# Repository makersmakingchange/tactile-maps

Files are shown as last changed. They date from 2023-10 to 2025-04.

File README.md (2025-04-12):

<!--- Open Source Assistive Technology: GitHub Readme Template --->
<!-- Template files available at https://github.com/makersmakingchange/OpenAT-Template -->

<!--- TITLE Should match the name of the GitHub repository. Choose something descriptive rather than whimsical.  --->
 # Tactile Maps

<!--- SUMMARY A brief summary of the project. What it does, who it is for, how much it costs.  --->
The Tactile Maps are designed to help users with visual impairments learn to navigate different types of intersections with various traffic signs and signals. Maps can be used separately as a learning tool for specific intersections and traffic signs and signals, or can be connected together to plan routes between locations.
The legend includes Braille labels for the different representations of traffic signs and signals.

<!--- PHOTO  --->
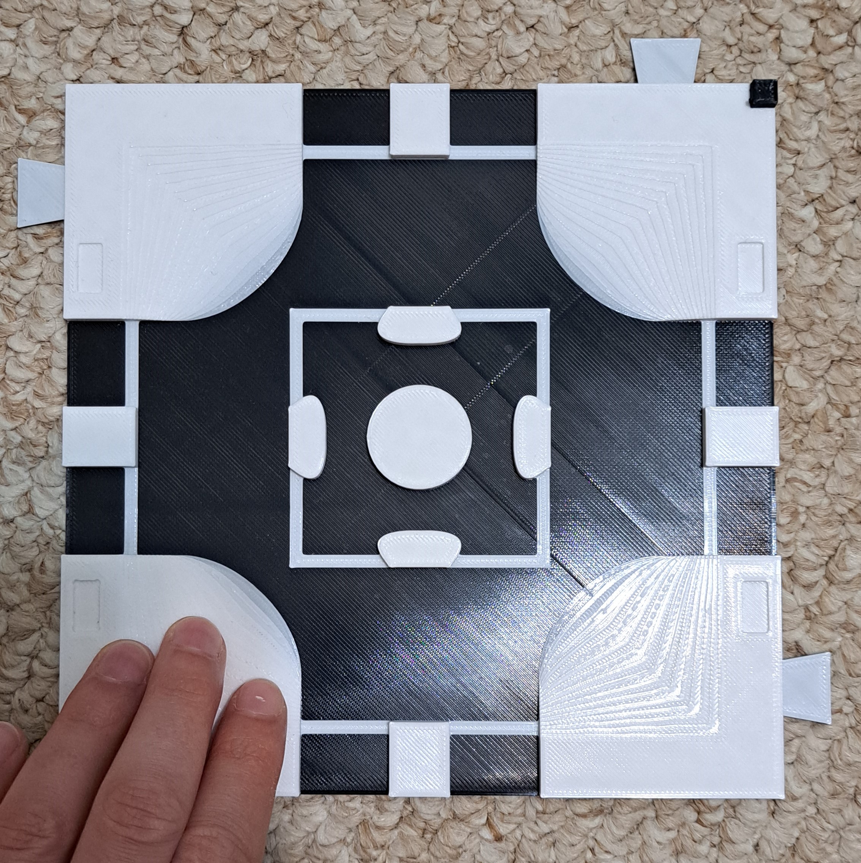
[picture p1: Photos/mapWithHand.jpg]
A user running their hand across the bottom of a tactile map representing a roundabout. The map has been attached to a carpet using hook and loop tape.


## Makers Making Change Assistive Device Library
 - https://www.makersmakingchange.com/s/product/tactile-maps/01tJR000000nEbJYAU

## Getting Started
<!--- 
Include an overall idea of what major steps are required to build the device.
 --->

### 1. Order the Off-The-Shelf Components
The [Bill of Materials](/Documentation/Tactile_Maps_BOM_v1.0.xlsx) lists all of the parts and components required to build the Tactile Maps.

### 2. Print the 3D Printable components
Print the components requested by the user.

All of the files and individual print files can be in the [/Build_Files/3D_Printing_Files](/Build_Files/3D_Printing_Files/) folder.

### 3. Assemble the Tactile Maps.
Reference the [Assembly Guide](/Documentation/Tactile_Maps_Maker_Guide_v1.0.pdf) for the tools and steps required to build the maps.

## Files
<!---
FILES
This section includes all the information and files required to build and modify the device, including documentation, design files, and build files. 
--->

### Documentation
<!---
DOCUMENTATION

--->
| Document | Version | Link |
|----------|---------|------|
| Design Rationale     | 1.0 | [Tactile_Maps_Design_Rationale](/Documentation/Tactile_Maps_Design_Rationale_v0.1.pdf) |
| Bill of Materials    | 1.0 | [Tactile_Maps_BOM](/Documentation/Tactile_Maps_BOM_v0.1.xlsx) |
| Maker Guide       | 1.0 | [Tactile_Maps_Instructions](/Documentation/Tactile_Maps_Maker_Guide_v0.1.pdf) |
| User Guide          | 1.0 | [Tactile_Maps_User_Guide](/Documentation/Tactile_Maps_User_Guide_v1.0.pdf)           |
| Changelog            | 1.0 | [Tactile_Maps_Changelog](/Documentation/Tactile_Maps_Changelog_v0.1.pdf)               |

### Design Files
<!---
DESIGN FILES
If possible, include a copy of original design files to facilitate easy editing and customization.
--->
 - [CAD Files](/Design_Files/CAD)

### Build Files
<!---
BUILD FILES
--->
 - [3D Printing Files](/Build_Files/3D_Printing)

## License
<!---
LICENSE
Choose an appropriate license. We recommend an open-source hardware compatible license.
--->
Everything needed or used to design, make, test, or prepare the Tactile Maps is licensed under the CERN 2.0 2.0 Permissive license <https://ohwr.org/project/cernohl/wikis/Documents/CERN-OHL-version-2> (CERN-OHL-P).

Accompanying material such as instruction manuals, videos, and other copyrightable works that are useful but not necessary to design, make, test, or prepare the Tactile Maps are published under a Creative Commons Attribution-ShareAlike 4.0 license <https://creativecommons.org/licenses/by-sa/4.0/> (CC BY-SA 4.0).

## Attribution
<!-- ATTRIBUTION -->

The documentation template was created by Makers Making Change and is used under a CC BY-SA 4.0 license. It is available at the following link: https://github.com/makersmakingchange/OpenAT-Template

----

<!-- ABOUT MMC START -->
## About Makers Making Change
[Makers Making Change Logo](https://www.makersmakingchange.com/)

Makers Making Change is a program of [Neil Squire](https://www.neilsquire.ca/), a Canadian non-profit that uses technology, knowledge, and passion to empower people with disabilities.

Makers Making Change leverages the capacity of community based Makers, Disability Professionals and Volunteers to develop and deliver affordable Open Source Assistive Technologies.

 - Website: [www.MakersMakingChange.com](https://www.makersmakingchange.com/)
 - GitHub: [makersmakingchange](https://github.com/makersmakingchange)
 - Bluesky: [@makersmakingchange.bsky.social](https://bsky.app/profile/makersmakingchange.bsky.social)
 - Instagram: [@makersmakingchange](https://www.instagram.com/makersmakingchange)
 - Facebook: [makersmakechange](https://www.facebook.com/makersmakechange)
 - LinkedIn: [Neil Squire Society](https://www.linkedin.com/company/neil-squire-society/)
 - Thingiverse: [makersmakingchange](https://www.thingiverse.com/makersmakingchange/about)
 - Printables: [MakersMakingChange](https://www.printables.com/@MakersMakingChange)

### Contact Us
For technical questions, to get involved, or to share your experience we encourage you to [visit our website](https://www.makersmakingchange.com/) or [contact us](https://www.makersmakingchange.com/s/contact).
<!-- ABOUT MMC END -->

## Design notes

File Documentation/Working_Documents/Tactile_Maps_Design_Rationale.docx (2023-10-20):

# Introduction

Tactile maps are often used to teach people with visual impairments how to navigate their surroundings. These maps can represent specific indoor and outdoor locations, or represent general information, such as a type of road intersection. Orientation and Mobility (OM) specialists often use tactile maps with their clients, but diagraming tools they use are not given to clients to take home and learn from. We wanted to create general maps of different road intersections that OM specialists could use with clients to teach how to navigate various generic intersections.

The tactile maps are intended for users with visual impairments. The maps could be used independently by people with visual impairments to study different types of intersections and can be used by OM specialists with clients.

It is important to note these maps are not designed to be an independent navigational tool. They are intended to help teach common features of different types of road intersections to help users with visual impairment learn to recognize different intersections. Relying on the maps for navigation could cause potential harm to users, such as getting lost or misidentifying an intersection.

# Research

Title | Touch Mapper
Link | https://touch-mapper.org/en/
Author | Samuli Pahaoja
License | Not stated, but open source
Cost | Cost of material, or starting at $29 USD for a printed map
Test Build (Y/N) | Y
Add to Library (Y/N) | N
Notes | Only outdoor maps are supported currently. Scale of maps are customizable, and maps can be printed in multiple parts. Maps do not include Braille labels or space for labels.

Title | Tactile Map Automated Production (TMAP)
Link | https://lighthouse-sf.org/tmap/
Author | Lighthouse for the Blind and Visually Impaired
License | Not listed
Cost | $26.25 USD for printed map, cost of materials if building own.
Test Build (Y/N) | N
Add to Library (Y/N) | N
Notes | Maps include Braille labels and legend. Maps designed to be embossed or printed on swell paper, not 3D printed.

Title | Picture Maker Wheatley Tactile Diagramming Kit
Link | https://www.aph.org/product/picture-maker-wheatley-tactile-diagramming-kit/
Author | Picture Maker
License | Not stated
Cost | $183 USD
Notes | Can quickly create tactile maps using pieces that attach to a felt background. Comes with various pieces that are simple shapes and high contrast colours.

# Requirements

## Goals

G01 | Create tactile maps of generic intersections (roundabouts, 4-way-stops, T-intersections, offset intersections, pedestrian crossings, and large intersections with corner islands)
G02 | Create representations of traffic signs/signals and common landmarks (bus stops, mailboxes)
G03 | Help users learn to navigate different intersections

## Functional Requirements

F01 | Features must be large enough and have enough space around them to be easily identified and differentiated through touch
F02 | Maps must be durable
F03 | Maps must accurately represent their respective intersections
F04 | Maps must include a legend to identify features such as traffic signs/signals
F05 | Maps should be simple to print in high contrast colours for users with partial sight

## Non-functional Requirement

NF01 | Maps must be easy to clean
NF02 | Maps must be easy to transport

## Constraints

C01 | Maps cannot contain too much information as they can become cluttered and difficult to interpret by touch
C02 | Maps must be low-cost

# Ideation

First concepts involved working from maps built through Touch Mapper, or through adapting Touch Mapper to suit the needs of the users. This idea was abandoned as it required a strong background in Python coding to adapt Touch Mapper, and converting STLs to modifiable models was computationally expensive. Creating the maps entirely was deemed to be both faster and a more suitable option for meeting the requestor’s needs.

# Conceptual Design

## Concept 1: Individual Maps

Initially, maps were designed to be individual pieces representing a specific intersection. These maps were designed to teach users common features of each intersection type.

## Concept 2: Connectable Maps

The second concept was to make maps which could be connected to build out routes between places. These would allow users to plan how they could move from one place to another by identifying the number and types of intersections they would need to pass through.

It is important to note that the maps should be considered a rough guide only and should not be used alone for route planning and navigation. Misidentifying the type and number of intersections on a route could cause a user to get lost or potentially come in harms way from crossing an intersection incorrectly.

# Prototyping

The first two prototypes were created to test the size of maps, height of the features, colour contrast, and the inclusion of Braille labels on the map. The larger map was 17x17x0.6 cm, and the smaller map was 8.5x8.5x0.32 cm. The maps also included Braille labels identifying the type of intersection they represented. There were not tabs used to connect the maps together as they were different sizes. The two prototypes are shown below:

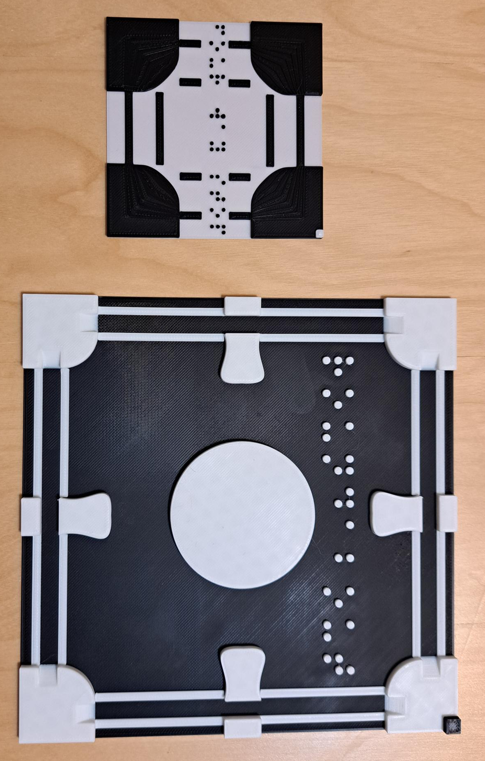
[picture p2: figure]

# Testing

The two prototype maps were sent to Orientation and Mobility specialists at Vision Loss Rehab in Burnaby, British Columbia. The users preferred the size of the larger map and the height of the features on that map. They also did not like having the Braille label in the middle of the map, as they felt users could have trouble differentiating the Braille labels from a feature on the map. The users also preferred the maps printed with white on black to the maps printed black on white. The subsequent maps were created at the size of the larger map, and Braille labels were removed from the maps themselves.

The clearance required for the pieces that insert into the maps, and the Braille labels for the legends were also tested. A clearance of 0.2 mm on each dimension, and dog boning of the holes with a 2 mm cutting tool diameter were found to be sufficient for a tight fit that was still easily removable.

# Detailed Design

All the maps use the same parameters, which can be found in the Fusion 360 file: TactileMapsParameters. The parameters are pulled from this file into all the others, so if someone wants to update the same parameter in all maps, they can update the TactileMapsParameters file only. The parameters are listed in the table below for users who do not have Fusion 360. Many of the parameters are built off others, such as the sidewalkWidth being one third of the length of the model.

Parameter Name | Value (mm) | Description
baseHeight | 0.4 | Height of the base of the model
clearance | 0.2 | Clearance around parts that will fit together
dogbone | 2 | Cutter diameter for creating dogbone corners.
featureHeight | 1.6 | Height of features such as bus stops
length | 170 | Side lengths of base of model
lineHeight | 0.3 | Height of crosswalk lines
lineWidth | 3 | Width of crosswalk lines
orientorHeight | 2.4 | Height of the orientation indicator
orientorSize | 6 | Side length of orientation indicator square
pegDepth | sidewalkHeight/4 | Depth of pegs/holes to connect features to map base
pegSize | 6 | Side length of pegs/holes to connect features to map base
sidewalkHeight | 3.2 | Height of sidewalk/walking surface
sidewalkWidth | length/3 | Width of the sidewalk/walking surface
tabHeight | sidewalkHeight/4 | Height of tabs to secure adjacent maps together
tabLength | length/14 | Length of tab to secure adjacent maps together
tabWidth | length/10 | Width of tabs to secure adjacent maps together

All the tactile maps have the road surface as the lowest surface, with any features raised above that. Painted pedestrian crossing lines are the second lowest feature and are raised to be felt by the user. Sidewalks and curbs are the third lowest feature, with curb cuts represented as gradual height increases and curbs as sudden changes in height (as they are in the real world). The features that can be slotted into the cut-outs on the sidewalks are the second highest level, allowing users to feel where and what a traffic sign may be. The highest feature on the map is a square in the top-right corner. This is used to orient the map and can represent North-East if planning a route. There are also tabs and cut-outs on the maps to connect and align them if they are being used together for route planning. All features are shown in the figures below.

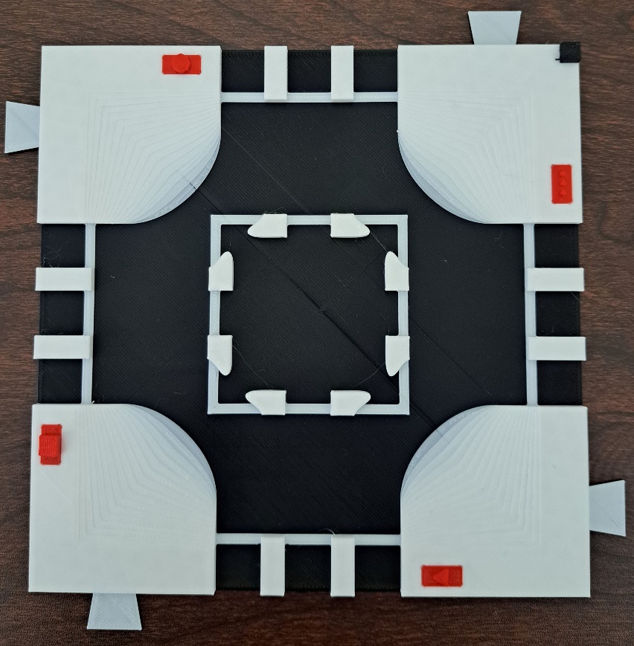
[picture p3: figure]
A tactile map of a large intersection. Different features are highlighted with different shaped boxes. A tab on the side used to connect maps together is circled in red, a stop sign piece is surrounded by a red rectangle, and the orientation indicator is surrounded by a red triangle.

The tabs on the sides of the maps are used to connect maps together. One of the tabs (top left) is circled in red. There are red pieces representing a stop sign, stop light, yield sign, and mailbox added to the map. The stop sign piece is surrounded by a red square. These pieces can be interchanged among maps and positions on the maps. The orientation square in the top right is surrounded by a red triangle.

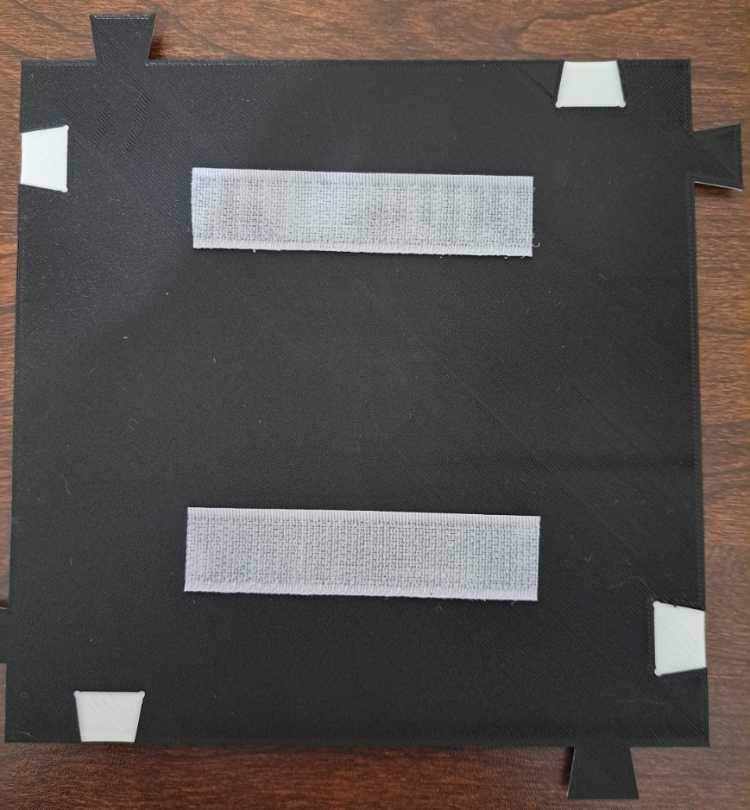
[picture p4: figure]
Hook side of hook and loop tape attached to the back of a tactile map. The cut-outs where tabs connect adjacent maps are circled in red.

The bottom of the map shows the corresponding cut-outs for the tabs on the sides. The tabs fit into the cut-outs to prevent the maps from shifting while users run their fingers over them. The cut-out on the top left has been circled in red. There is also hook and loop tape attached to the bottom of the map to allow it to be mounted to another surface. The hook side of the tape has been connected to the map.

There is also a legend with Braille labels to help users identify different features such as traffic signs/signals.

From top to bottom the symbols represent a stop sign, a yield sign, a mailbox, a bus stop, a bike lane, a stop light, rail tracks, and a pedestrian crossing. The labels read: “stop”, “yield”, “mailbox”, “bus stop”, “bike lane”, “stop light”, “rail crossing”, and “pedestrian crossing”.

# Opportunities for Improvement

- Improving alignment/connection design
  - Current tabs can break easily
  - Current tabs could connect maps more securely
  - Could use bowtie shaped pieces to hold the maps together
- Including method to create custom maps for individual users (with Orientation and Mobility specialist consultation)
- Including space for 3D printed Braille labels for each map
- Create standard text tactile legend

© 2023 by Neil Squire. This work is licensed under the CC BY SA 4.0 License: http://creativecommons.org/licenses/by-sa/4.0 Files available at https://makersmakingchange.com/project/tactile-maps/ Page 1 of 1

V1.0 | May 2023 Tactile Maps Design Rationale

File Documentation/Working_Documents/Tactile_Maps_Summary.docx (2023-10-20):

# Title

Tactile Maps

## Subtitle

3D printed Tactile Maps for people with visual impairments. The general maps represent different intersections and common road signs.

## Device Specifications

Build Time:

< 1hr

1-4 hr

5-10hr

>10hr

Cost:

$0 - $10

$11 - $25

$26 - $50

$51 - $100

$101 - $250

$250+

Stage:

- Recently added

Skills:

- 3D printing

Need:

- Orientation and mobility

Disability:

- Visual impairment

Difficulty:

- Easy

License:

- Attribution – ShareAlike 4.0 International

Usages:

- Orientation and mobility

Type:

- Assistive device

Designer:

- Stephan Dobri – Makers Making Change

## Device Details

### Overview

The Tactile Maps are designed to help users with visual impairments learn to navigate different types of intersections with various traffic signs and signals. Maps can be used separately as a learning tool for specific intersections and traffic signs and signals, or can be connected together to plan routes between locations.

The legend includes Braille labels for the different representations of traffic signs and signals.

### Usage

Use the map on a surface where it will not slide around as the user runs their hands over the map. If the map has hook and loop tape, the maps can be attached to any surface the hook side will attach to, including carpet or tactile map diagramming kit backboards. Insert the desired traffic sign/signal pieces into the spaces on the tactile maps being used. The pieces should fit snuggly into the cut-outs on the tops of the maps and not get knocked out when running your hand over the features. They should still be easy to remove and change different pieces.

There is a raised square in the top-right corner of the map to help users orient to the direction of the maps. For example, this corner could represent North-East.

A user will run their hands over the maps to feel the different road features, including crosswalk lines, sidewalks/pavement, and traffic signs/signals.

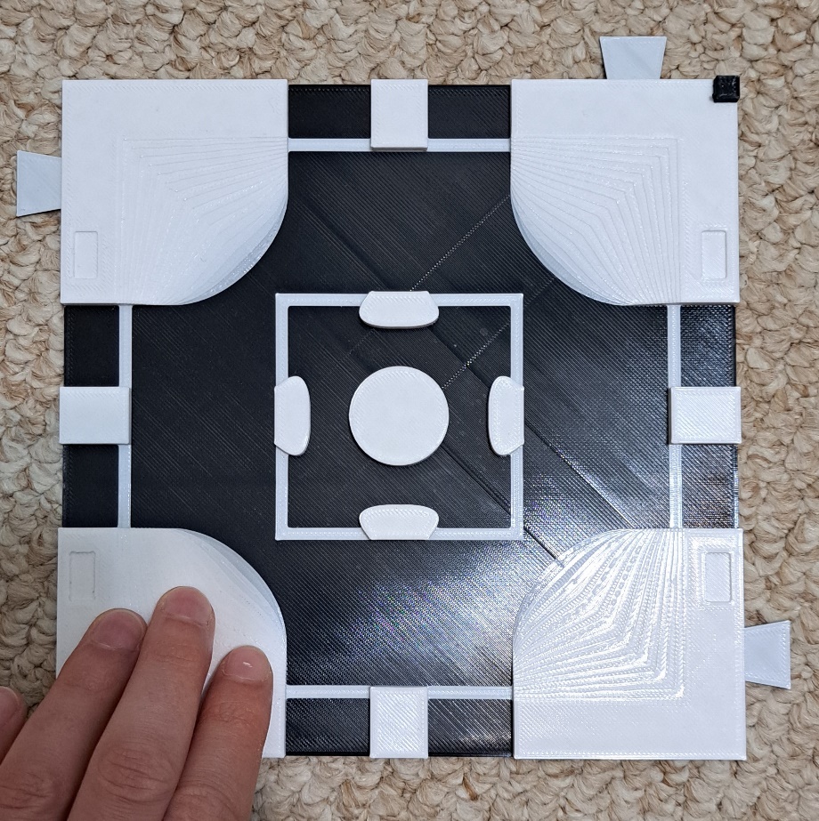
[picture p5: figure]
A user running their hand across the bottom of a tactile map representing a roundabout. The map has been attached to a carpet using hook and loop tape.

If they are unsure what a feature represents, they can consult the legend if they read Braille. If they do not read Braille, the different signs and signals are shown below.

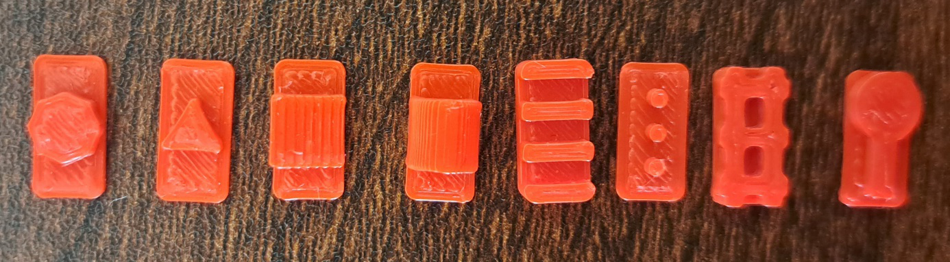
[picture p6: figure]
3D printed features that represent from left to right: Stop signs, yield signs, mailboxes, bus stops, bike lanes, stop signs, railroad crossings, and pedestrian crossings.

3D printed features that represent from left to right: Stop signs, yield signs, mailboxes, bus stops, bike lanes, stop signs, railroad tracks, and pedestrian crossings.

Maps can also be connected to represent a route between places in a city. For example, if someone had to walk through an offset intersection then to a pedestrian crossing, the two maps could be connected as shown below.

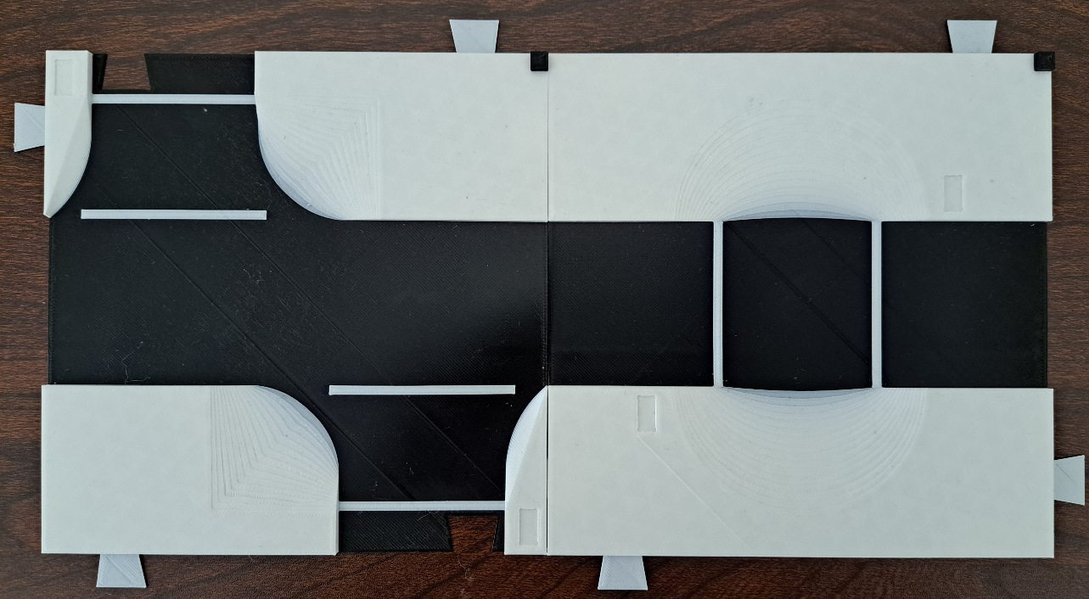
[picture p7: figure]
Two tactile maps connected together by the tabs on the edges of the maps. The two maps represent an offset intersection and pedestrian crossing.

### Cost

Printing all six tactile maps, the legend, Braille labels, and feature pieces, and adding hook and loop tape to each map and the legend costs $13.00. If a user does not want hook and loop tape, or a different combination of maps and features the cost will change.

### Build Instructions

This build consists solely of 3D printing.

#### Skills Required

3D printing

#### Time Required

The total time to print all six maps, the legend, Braille labels, and feature pieces is 35 hours and 20 minutes. There is a detailed breakdown of how long each piece takes to print in the Bill of Materials (BOM), and Maker Guide.

Assembling the legend will take under five minutes.

#### Tools

Scissors (optional)

Super glue (optional)

#### Components

Hook and loop tape (optional)

#### 3D Printing

- Tactile maps legend
- Four way stop map
- Large intersection map
- Offset intersection map
- Pedestrian crossing map
- Roundabout map
- T-intersection map
- Bike lane piece
- Bike lane label
- Bus stop piece
- Bus stop label
- Mailbox piece
- Mailbox label
- Pedestrian crossing piece
- Pedestrian crossing label
- Rail crossing piece
- Rail crossing label
- Stop light piece
- Stop light label
- Stop sign piece
- Stop sign label
- Yield sign piece
- Yield sign label

### Design

### Attribution

This design was requested by employees of Vision Loss Rehab in British Columbia.

Original design by: Stephan Dobri – Makers Making Change under an Attribution – ShareAlike 4.0 International license.

The orientation indicator was based on the indicator used by Touch Mapper (https://touch-mapper.org/en/).

© 2023 by Neil Squire. This work is licensed under the CC BY SA 4.0 License: http://creativecommons.org/licenses/by-sa/4.0 Files available at https://makersmakingchange.com/project/tactile-maps/ Page 1 of 2

V1.0 | May 2023 Tactile Maps Summary

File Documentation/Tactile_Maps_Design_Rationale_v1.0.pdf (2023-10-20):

V1.0 | May 2023

## Tactile Maps

## DESIGN RATIONALE

© 2023 by Neil Squire. (https://neilsquire.ca/)
This work is licensed under the CC BY SA 4.0 License: http://creativecommons.org/licenses/by-sa/4.0 Files available at https://makersmakingchange.com/project/tactile-maps/

### Introduction

Tactile maps are often used to teach people with visual impairments how to navigate their surroundings. These maps can represent specific indoor and outdoor locations, or represent general information, such as a type of road intersection. Orientation and Mobility (OM) specialists often use tactile maps with their clients, but diagraming tools they use are not given to clients to take home and learn from. We wanted to create general maps of different road intersections that OM specialists could use with clients to teach how to navigate various generic intersections.

The tactile maps are intended for users with visual impairments. The maps could be used independently by people with visual impairments to study different types of intersections and can be used by OM specialists with clients.

It is important to note these maps are not designed to be an independent navigational tool. They are intended to help teach common features of different types of road intersections to help users with visual impairment learn to recognize different intersections. Relying on the maps for navigation could cause potential harm to users, such as getting lost or misidentifying an intersection.

### Research

Title | Touch Mapper
Link | https://touch-mapper.org/en/
Author | Samuli Pahaoja
License | Not stated, but open source
Cost | Cost of material, or starting at $29 USD for a printed map
Test Build (Y/N) | Y
Add to Library (Y/N) | N
Notes | Only outdoor maps are supported currently. Scale of maps are customizable, and maps can be printed in multiple parts. Maps do not include Braille labels or space for labels.
Title | Tactile Map Automated Production (TMAP)
Link | https://lighthouse-sf.org/tmap/
Author | Lighthouse for the Blind and Visually Impaired
License | Not listed
Cost | $26.25 USD for printed map, cost of materials if building own.
Test Build (Y/N) | N
Add to Library (Y/N) | N

## DESIGN RATIONALE

© 2023 by Neil Squire. (https://neilsquire.ca/)

Notes | Maps include Braille labels and legend. Maps designed to be embossed or printed on swell paper, not 3D printed.
Title | Picture Maker Wheatley Tactile Diagramming Kit
Link | https://www.aph.org/product/picture-maker-wheatley-tactile-diagramming-kit/ (https://www.aph.org/product/picture-maker-wheatley-tactile-diagramming-kit/)
Author | Picture Maker
License | Not stated
Cost | $183 USD
Notes | Can quickly create tactile maps using pieces that attach to a felt background. Comes with various pieces that are simple shapes and high contrast colours.

### Requirements

### Goals

G01 | Create tactile maps of generic intersections (roundabouts, 4-way-stops, T-intersections, offset intersections, pedestrian crossings, and large intersections with corner islands)
G02 | Create representations of traffic signs/signals and common landmarks (bus stops, mailboxes)
G03 | Help users learn to navigate different intersections

### Functional Requirements

F01 | Features must be large enough and have enough space around them to be easily identified and differentiated through touch
F02 | Maps must be durable
F03 | Maps must accurately represent their respective intersections
F04 | Maps must include a legend to identify features such as traffic signs/signals
F05 | Maps should be simple to print in high contrast colours for users with partial sight

### Non-functional Requirement

NF01 | Maps must be easy to clean
NF02 | Maps must be easy to transport

### Constraints

C01 Maps cannot contain too much information as they can become cluttered and difficult to interpret by touch

## DESIGN RATIONALE

© 2023 by Neil Squire. (https://neilsquire.ca/)

C02 Maps must be low-cost

### Ideation

First concepts involved working from maps built through Touch Mapper, or through adapting Touch Mapper to suit the needs of the users. This idea was abandoned as it required a strong background in Python coding to adapt Touch Mapper, and converting STLs to modifiable models was computationally expensive. Creating the maps entirely was deemed to be both faster and a more suitable option for meeting the requestor’s needs.

### Conceptual Design

### Concept 1: Individual Maps

Initially, maps were designed to be individual pieces representing a specific intersection. These maps were designed to teach users common features of each intersection type.

### Concept 2: Connectable Maps

The second concept was to make maps which could be connected to build out routes between places. These would allow users to plan how they could move from one place to another by identifying the number and types of intersections they would need to pass through.

It is important to note that the maps should be considered a rough guide only and should not be used alone for route planning and navigation. Misidentifying the type and number of intersections on a route could cause a user to get lost or potentially come in harms way from crossing an intersection incorrectly.

### Prototyping

The first two prototypes were created to test the size of maps, height of the features, colour contrast, and the inclusion of Braille labels on the map. The larger map was 17x17x0.6 cm, and the smaller map was 8.5x8.5x0.32 cm. The maps also included Braille labels identifying the type of intersection they represented. There were not tabs used to connect the maps together as they were different sizes. The two prototypes are shown below:

## DESIGN RATIONALE

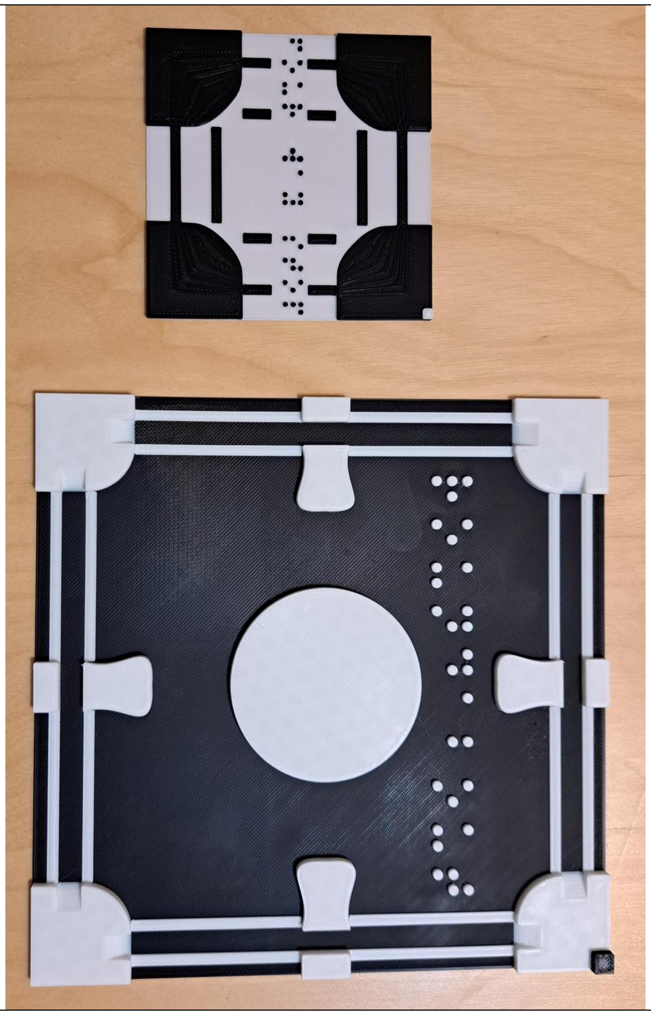
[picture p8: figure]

© 2023 by Neil Squire. (https://neilsquire.ca/)

### Testing

The two prototype maps were sent to Orientation and Mobility specialists at Vision Loss Rehab in Burnaby, British Columbia. The users preferred the size of the larger map and the height of the features on that map. They also did not like having the Braille label in the middle of the map, as they felt users

## DESIGN RATIONALE

© 2023 by Neil Squire. (https://neilsquire.ca/)

could have trouble differentiating the Braille labels from a feature on the map. The users also preferred the maps printed with white on black to the maps printed black on white. The subsequent maps were created at the size of the larger map, and Braille labels were removed from the maps themselves.

The clearance required for the pieces that insert into the maps, and the Braille labels for the legends were also tested. A clearance of 0.2 mm on each dimension, and dog boning of the holes with a 2 mm cutting tool diameter were found to be sufficient for a tight fit that was still easily removable.

### Detailed Design

All the maps use the same parameters, which can be found in the Fusion 360 file: TactileMapsParameters. The parameters are pulled from this file into all the others, so if someone wants to update the same parameter in all maps, they can update the TactileMapsParameters file only. The parameters are listed in the table below for users who do not have Fusion 360. Many of the parameters are built off others, such as the sidewalkWidth being one third of the length of the model.

Parameter Name | Value (mm) | Description
baseHeight | 0.4 | Height of the base of the model
clearance | 0.2 | Clearance around parts that will fit together
dogbone | 2 | Cutter diameter for creating dogbone corners.
featureHeight | 1.6 | Height of features such as bus stops
length | 170 | Side lengths of base of model
lineHeight | 0.3 | Height of crosswalk lines
lineWidth | 3 | Width of crosswalk lines
orientorHeight | 2.4 | Height of the orientation indicator
orientorSize | 6 | Side length of orientation indicator square
pegDepth | sidewalkHeight/4 | Depth of pegs/holes to connect features to map base
pegSize | 6 | Side length of pegs/holes to connect features to map base
sidewalkHeight | 3.2 | Height of sidewalk/walking surface
sidewalkWidth | length/3 | Width of the sidewalk/walking surface
tabHeight | sidewalkHeight/4 | Height of tabs to secure adjacent maps together
tabLength | length/14 | Length of tab to secure adjacent maps together

## DESIGN RATIONALE

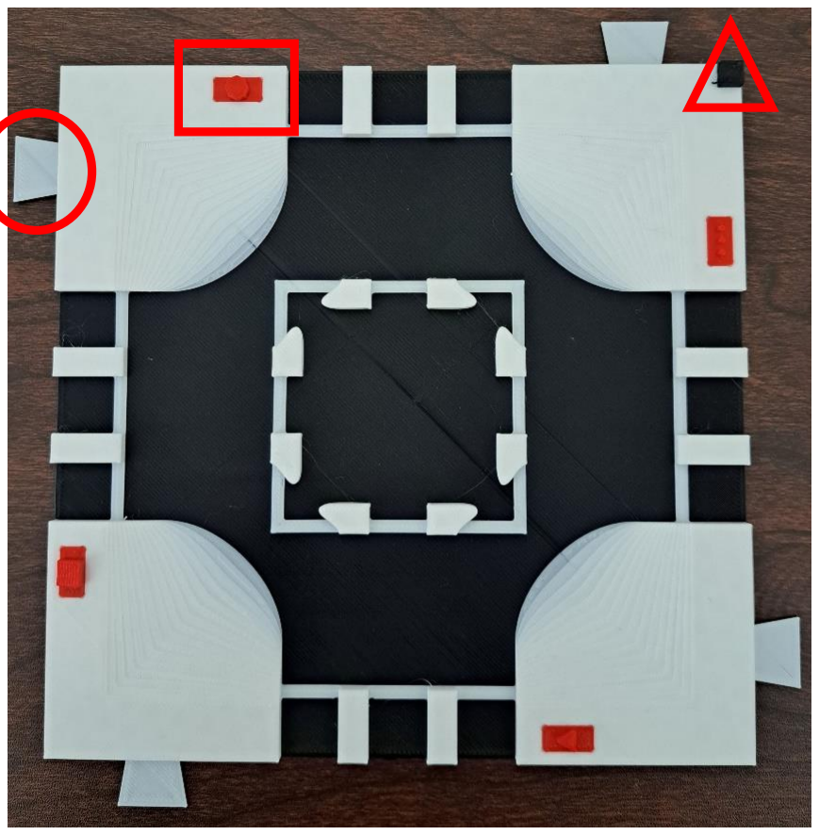
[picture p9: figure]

© 2023 by Neil Squire. (https://neilsquire.ca/)

tabWidth | length/10 | Width of tabs to secure adjacent maps together

All the tactile maps have the road surface as the lowest surface, with any features raised above that. Painted pedestrian crossing lines are the second lowest feature and are raised to be felt by the user. Sidewalks and curbs are the third lowest feature, with curb cuts represented as gradual height increases and curbs as sudden changes in height (as they are in the real world). The features that can be slotted into the cut-outs on the sidewalks are the second highest level, allowing users to feel where and what a traffic sign may be. The highest feature on the map is a square in the top-right corner. This is used to orient the map and can represent North-East if planning a route. There are also tabs and cut-outs on the maps to connect and align them if they are being used together for route planning. All features are shown in the figures below.

The tabs on the sides of the maps are used to connect maps together. One of the tabs (top left) is circled in red. There are red pieces representing a stop sign, stop light, yield sign, and mailbox added to the map. The stop sign piece is surrounded by a red square. These pieces can be interchanged among maps and positions on the maps. The orientation square in the top right is surrounded by a red triangle.

## DESIGN RATIONALE

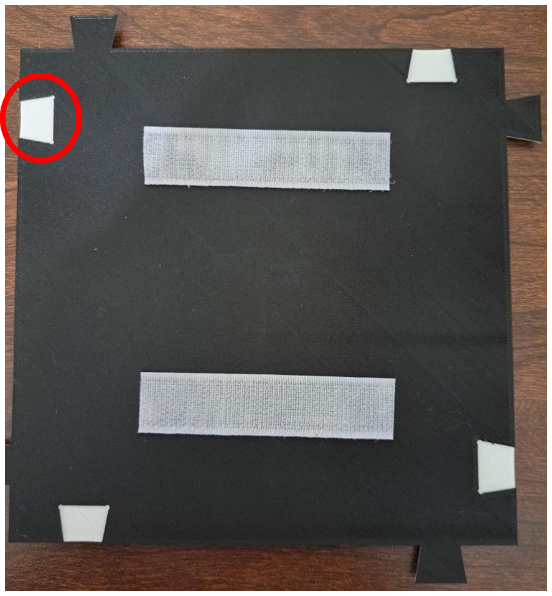
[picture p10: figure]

© 2023 by Neil Squire. (https://neilsquire.ca/)

The bottom of the map shows the corresponding cut-outs for the tabs on the sides. The tabs fit into the cut-outs to prevent the maps from shifting while users run their fingers over them. The cut-out on the top left has been circled in red. There is also hook and loop tape attached to the bottom of the map to allow it to be mounted to another surface. The hook side of the tape has been connected to the map.

There is also a legend with Braille labels to help users identify different features such as traffic signs/signals.

From top to bottom the symbols represent a stop sign, a yield sign, a mailbox, a bus stop, a bike lane, a stop light, rail tracks, and a pedestrian crossing. The labels read: “stop”, “yield”, “mailbox”, “bus stop”, “bike lane”, “stop light”, “rail crossing”, and “pedestrian crossing”.

### Opportunities for Improvement

- Improving alignment/connection design
- Current tabs can break easily
- Current tabs could connect maps more securely

## DESIGN RATIONALE

© 2023 by Neil Squire. (https://neilsquire.ca/)

- Could use bowtie shaped pieces to hold the maps together
- Including method to create custom maps for individual users (with Orientation and Mobility specialist consultation)
- Including space for 3D printed Braille labels for each map
- Create standard text tactile legend

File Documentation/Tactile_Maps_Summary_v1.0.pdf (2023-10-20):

V1.0 | May 2023

## Tactile Maps

## SUMMARY

© 2023 by Neil Squire. (https://neilsquire.ca/)
This work is licensed under the CC BY SA 4.0 License: http://creativecommons.org/licenses/by-sa/4.0 Files available at https://makersmakingchange.com/project/tactile-maps/

### Title

Tactile Maps

### Subtitle

3D printed Tactile Maps for people with visual impairments. The general maps represent different intersections and common road signs.

### Device Specifications

Build Time:

< 1hr

1-4 hr

5-10hr

>10hr

Cost:

$0 - $10

$11 - $25

$26 - $50

$51 - $100

$101 - $250

$250+

Stage:

- Recently added

Skills:

- 3D printing

Need:

- Orientation and mobility

Disability:

- Visual impairment

## SUMMARY

© 2023 by Neil Squire. (https://neilsquire.ca/)

Difficulty:

- Easy

License:

- Attribution – ShareAlike 4.0 International

Usages:

- Orientation and mobility

Type:

- Assistive device

Designer:

- Stephan Dobri – Makers Making Change

### Device Details

Overview
The Tactile Maps are designed to help users with visual impairments learn to navigate different types of intersections with various traffic signs and signals. Maps can be used separately as a learning tool for specific intersections and traffic signs and signals, or can be connected together to plan routes between locations.

The legend includes Braille labels for the different representations of traffic signs and signals.

Usage
Use the map on a surface where it will not slide around as the user runs their hands over the map. If the map has hook and loop tape, the maps can be attached to any surface the hook side will attach to, including carpet or tactile map diagramming kit backboards. Insert the desired traffic sign/signal pieces into the spaces on the tactile maps being used. The pieces should fit snuggly into the cut-outs on the tops of the maps and not get knocked out when running your hand over the features. They should still be easy to remove and change different pieces.

There is a raised square in the top-right corner of the map to help users orient to the direction of the maps. For example, this corner could represent North-East.

A user will run their hands over the maps to feel the different road features, including crosswalk lines, sidewalks/pavement, and traffic signs/signals.

## SUMMARY

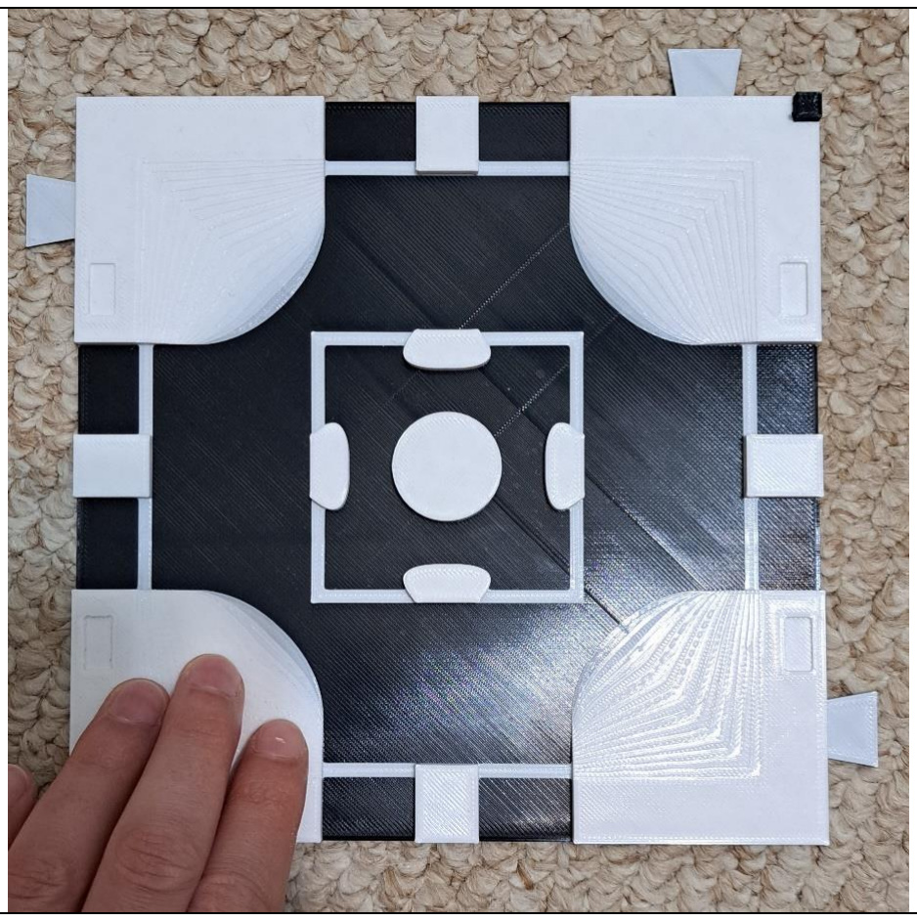
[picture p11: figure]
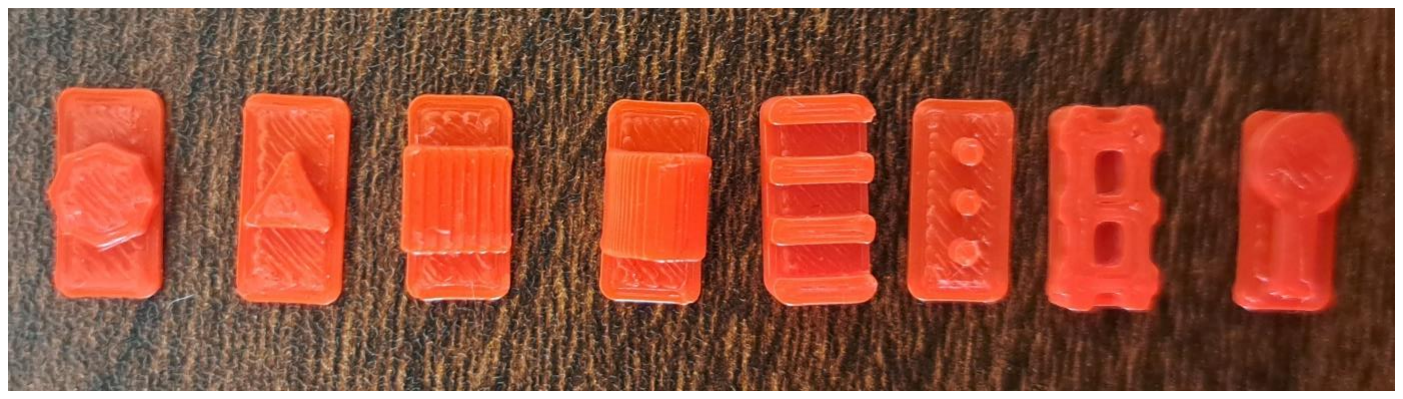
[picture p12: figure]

© 2023 by Neil Squire. (https://neilsquire.ca/)

If they are unsure what a feature represents, they can consult the legend if they read Braille. If they do not read Braille, the different signs and signals are shown below.

3D printed features that represent from left to right: Stop signs, yield signs, mailboxes, bus stops, bike lanes, stop signs, railroad tracks, and pedestrian crossings.

Maps can also be connected to represent a route between places in a city. For example, if someone had to walk through an offset intersection then to a pedestrian crossing, the two maps could be connected as shown below.

## SUMMARY

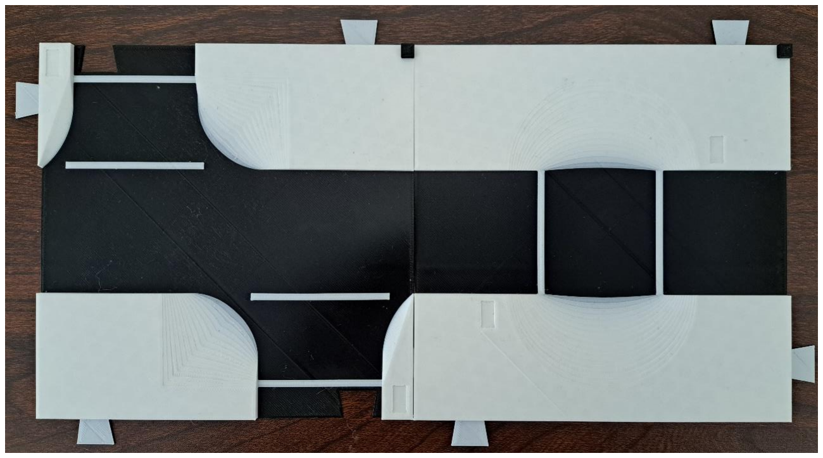
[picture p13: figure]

© 2023 by Neil Squire. (https://neilsquire.ca/)

Cost
Printing all six tactile maps, the legend, Braille labels, and feature pieces, and adding hook and loop tape to each map and the legend costs $13.00. If a user does not want hook and loop tape, or a different combination of maps and features the cost will change.

Build Instructions
This build consists solely of 3D printing.

Skills Required
3D printing

Time Required
The total time to print all six maps, the legend, Braille labels, and feature pieces is 35 hours and 20 minutes. There is a detailed breakdown of how long each piece takes to print in the Bill of Materials (BOM), and Maker Guide.

Assembling the legend will take under five minutes.

Tools
Scissors (optional)

Super glue (optional)

## SUMMARY

© 2023 by Neil Squire. (https://neilsquire.ca/)

Components
Hook and loop tape (optional)

3D Printing
- Tactile maps legend
- Four way stop map
- Large intersection map
- Offset intersection map
- Pedestrian crossing map
- Roundabout map
- T-intersection map
- Bike lane piece
- Bike lane label
- Bus stop piece
- Bus stop label
- Mailbox piece
- Mailbox label
- Pedestrian crossing piece
- Pedestrian crossing label
- Rail crossing piece
- Rail crossing label
- Stop light piece
- Stop light label
- Stop sign piece
- Stop sign label
- Yield sign piece
- Yield sign label

Design

Attribution
This design was requested by employees of Vision Loss Rehab in British Columbia.

Original design by: Stephan Dobri – Makers Making Change under an Attribution – ShareAlike 4.0 International license.

The orientation indicator was based on the indicator used by Touch Mapper. (https://touch-mapper.org/en/)

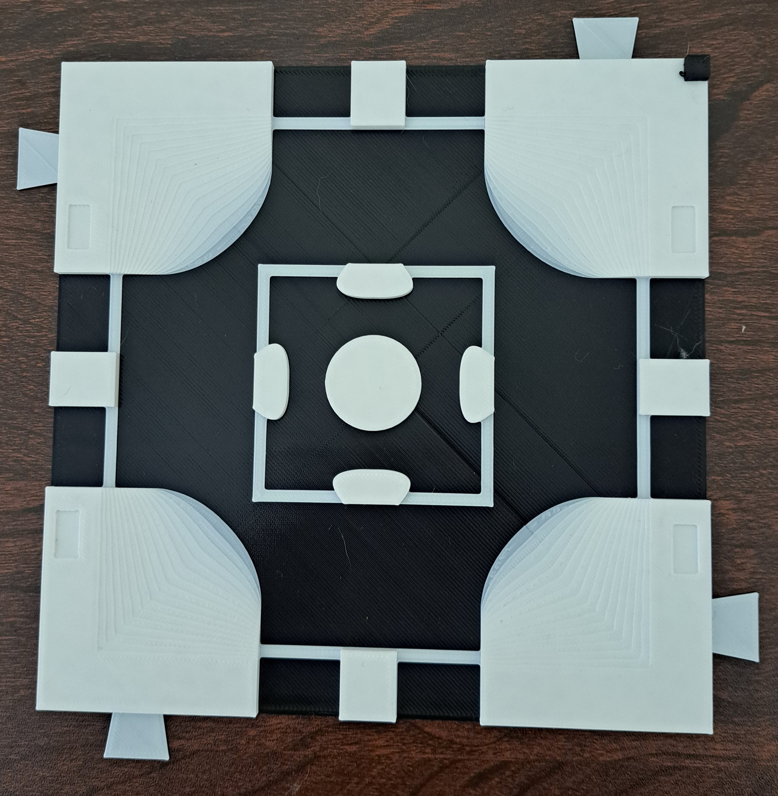
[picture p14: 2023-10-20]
Photos/Roundabout.jpg

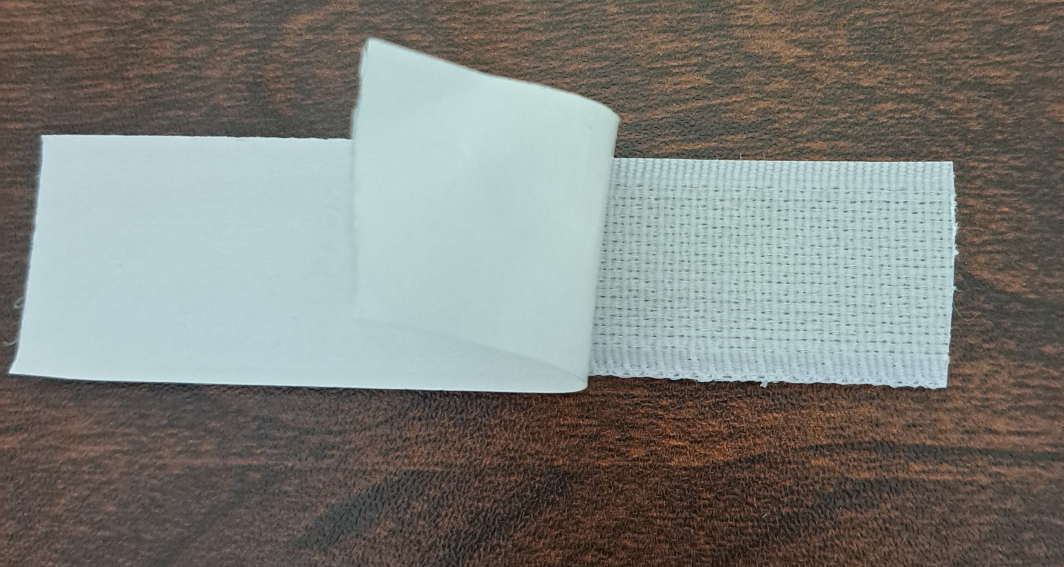
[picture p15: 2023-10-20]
Photos/peelingHook.jpg

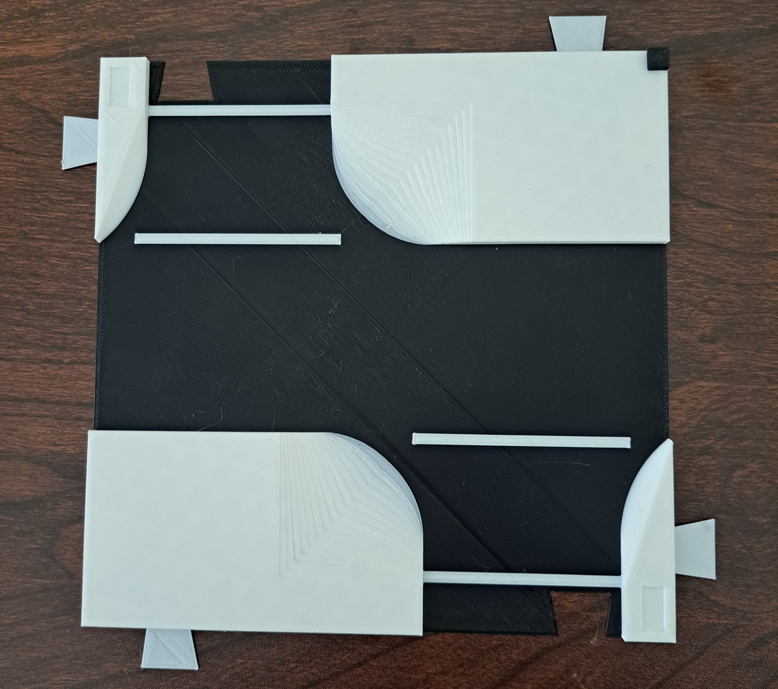
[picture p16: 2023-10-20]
Photos/offsetIntersection.jpg

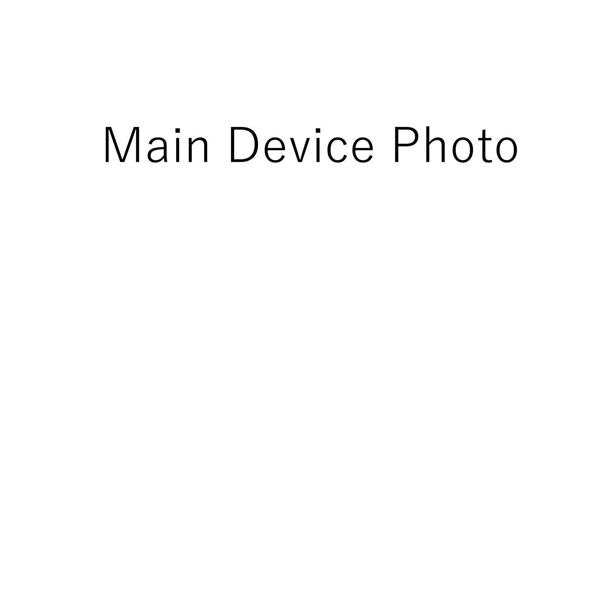
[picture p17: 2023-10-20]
Photos/Device-Name.jpg

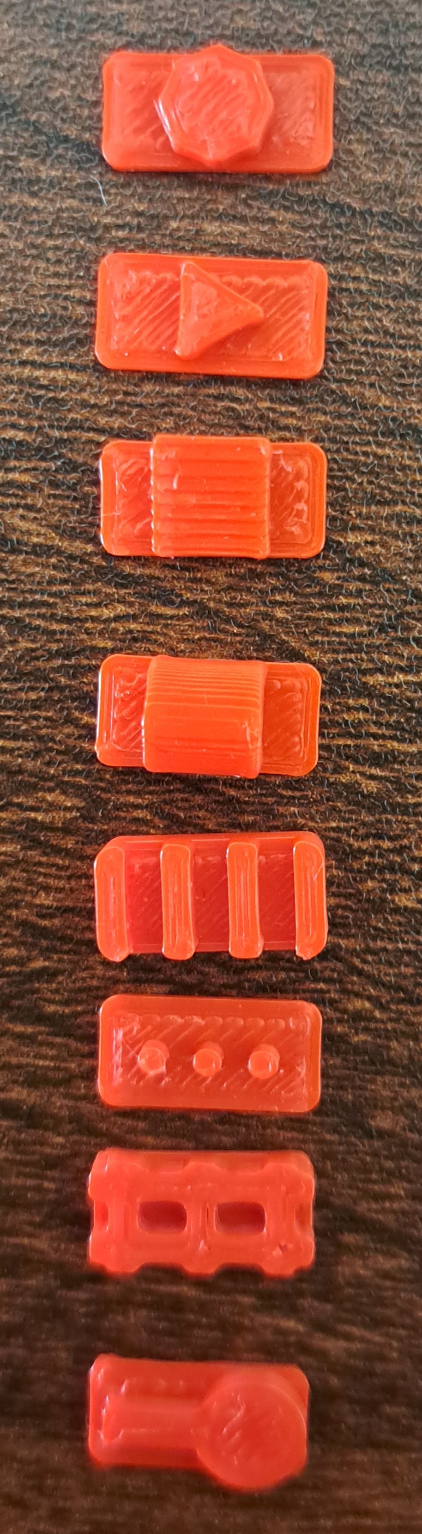
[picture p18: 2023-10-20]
Photos/featurePieces.jpg

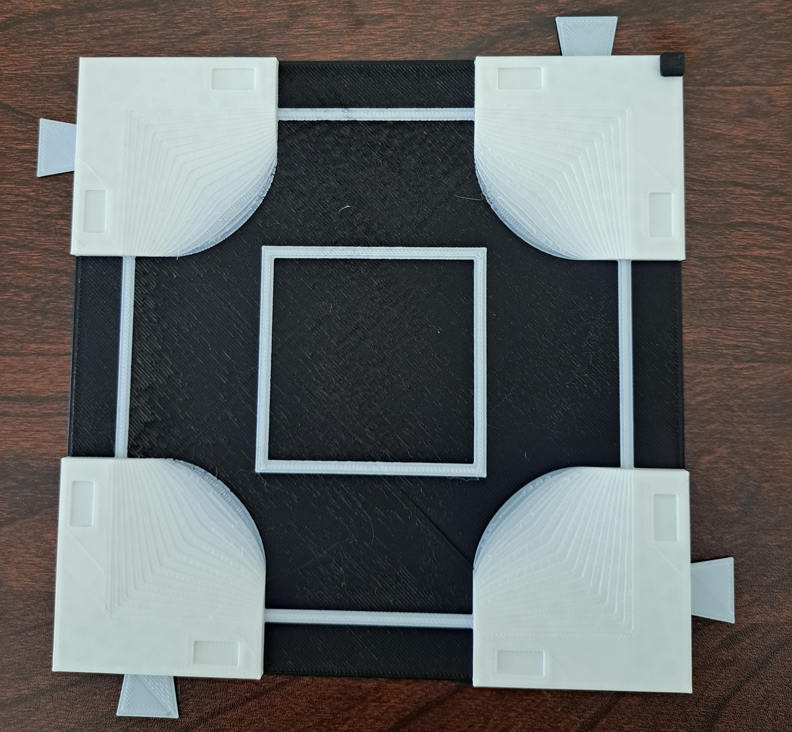
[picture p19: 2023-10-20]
Photos/fourWayStop.jpg

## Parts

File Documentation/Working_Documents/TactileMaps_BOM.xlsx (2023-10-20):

Device: Tactile Maps |  | Total Cost | Total Print time (hr) | Total filament (g)
Version: V1.0 | Date Created: May 2023 | $12.84 | 35.33 | 289
Commercial Parts:
Part type (Electrical. Mechanical, Sanitization, ect) | Part Name | Quantity Needed (cm) | Pkg Quantity (cm) | Price per package | Price per Unit | Price for qty needed |  | Link
Mechanical | Hook and loop tape | 208 | 1000 | $27.00 | $0.03 | $5.62 | https://www.amazon.ca/Adhesive-Fastener-Compatibility-Mounting-Tape%EF%BC%881IN/dp/B0BWXG8FKS?hvadid=636772209831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
 |  |  |  |  |  | $0.00
 |  |  |  |  |  | $0.00
3D Printed Parts ESTIMATED PRICING USING 1KG ROLL COST: | $25.00
Part | Description | Quantity Needed | TOTAL Mass (g) | Estimated Price | Print Time (Min) | Link
Legend | Legend of features on maps | 1 | 14 | $0.35 | 116
Four Way Stop Map | Map of a four way stop | 1 | 38 | $0.95 | 280
Large Intersection Map | Map of a large intersection with corner islands | 1 | 42 | $1.05 | 316
Offset Intersection Map | Map of an offset intersection | 1 | 39 | $0.97 | 279
Pedestrian Crossing Map | Map of a midblock pedestrian crossing | 1 | 53 | $1.32 | 362
Roundabout Map | Map of a roundabout | 1 | 43 | $1.07 | 317
T Intersection Map | Map of a T intersection | 1 | 47 | $1.18 | 324
Bike Lane Piece | Piece to represent a bike lane | 1 | 0.125 | $0.003125 | 1
Bike Lane Label | Braille label of a bike lane for the legend | 1 | 1 | $0.03 | 13
Bus Stop Piece | Piece to represent a bus stop | 1 | 0.125 | $0.003125 | 2
Bus Stop Label | Braille label of a bus stop for the legend | 1 | 1 | $0.03 | 12
Mailbox Piece | Piece to represent a mailbox | 1 | 0.125 | $0.003125 | 2
Mailbox Label | Braille label of a mailbox for the legend | 1 | 1 | $0.03 | 11
Pedestrian Crossing Piece | Piece to represent a pedestrian crossing | 1 | 0.125 | $0.003125 | 2
Pedestrian Crossing Label | Braille label of a pedestrian crossing for the legend | 1 | 3 | $0.07 | 26
Rail Crossing Piece | Piece to represent a rail crossing | 1 | 0.125 | $0.003125 | 2
Rail Crossing Label | Braille label of a rail crossing for the legend | 1 | 2 | $0.05 | 18
Stop Light Piece | Piece to represent a stop light | 1 | 0.125 | $0.003125 | 1
Stop Light Label | Braille label of a stop light for the legend | 1 | 2 | $0.05 | 14
Stop Sign Piece | Piece to respresent a stop sign | 1 | 0.125 | $0.003125 | 1
Stop Sign Label | Braille label of a stop sign for the legend | 1 | 1 | $0.03 | 10
Yield Sign Piece | Piece to represent a yield sign | 1 | 0.125 | $0.003125 | 1
Yield Sign Label | Braille label of a yield sign for the legend | 1 | 1 | $0.03 | 10
 |  |  | Total Print Cost: | $7.23
Tools for Assembly
Super glue (optional)
Alternatives (if there are other sources for some parts link them below)
Part and description | Link

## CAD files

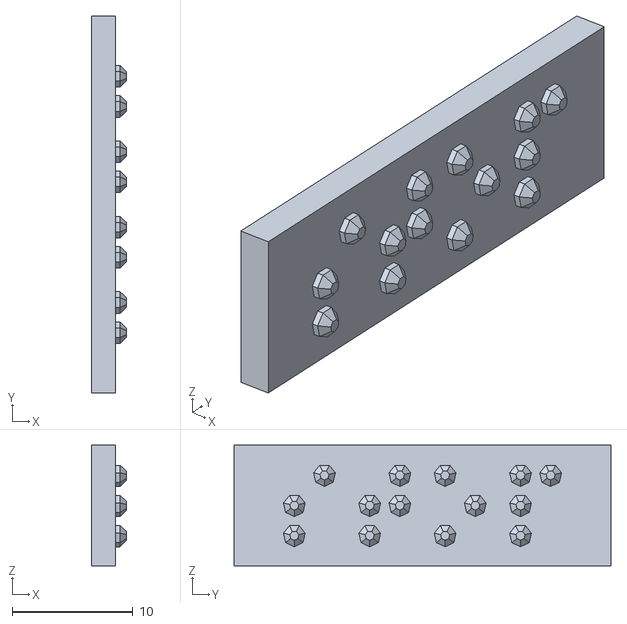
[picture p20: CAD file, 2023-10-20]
Build_Files/3D_Printing_Files/stopSignLabel.stl
2.92 x 31.2 x 10.0

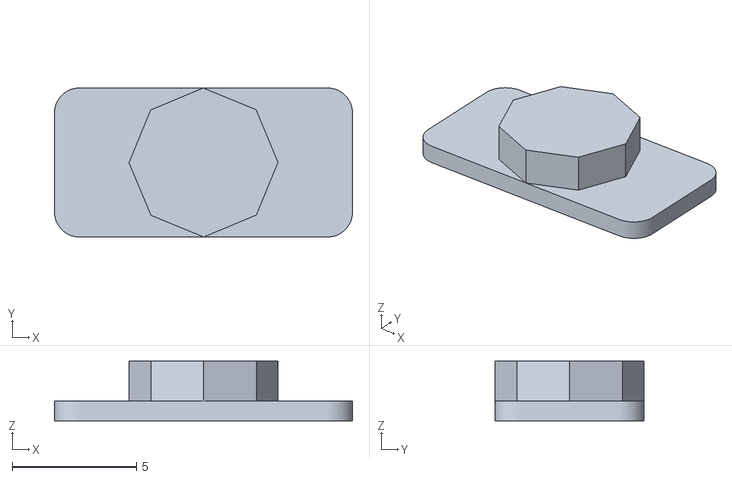
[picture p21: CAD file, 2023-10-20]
Build_Files/3D_Printing_Files/stopSignPiece.stl
12.0 x 6.00 x 2.40

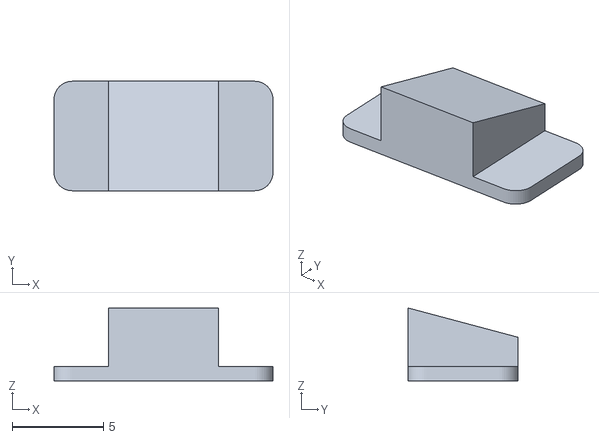
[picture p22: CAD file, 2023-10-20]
Build_Files/3D_Printing_Files/mailBoxPiece.stl
12.0 x 6.00 x 4.00

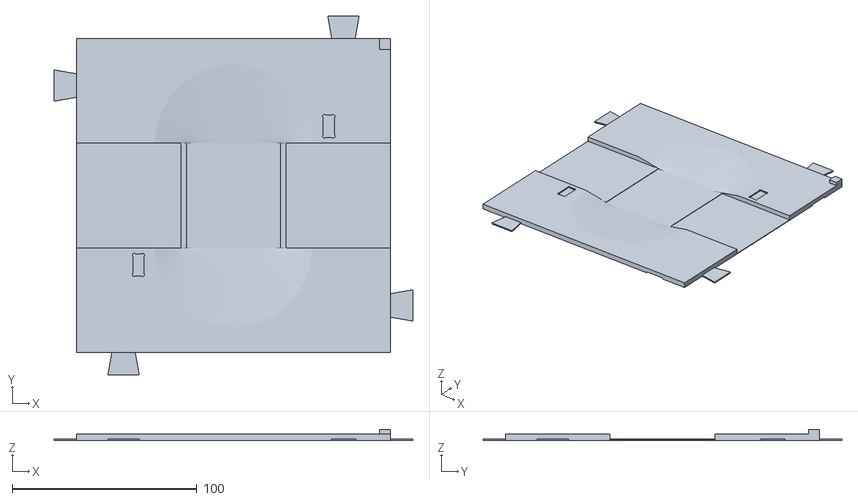
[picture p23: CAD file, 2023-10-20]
Build_Files/3D_Printing_Files/pedestrianCrossingMap.stl
194.3 x 194.3 x 6.00

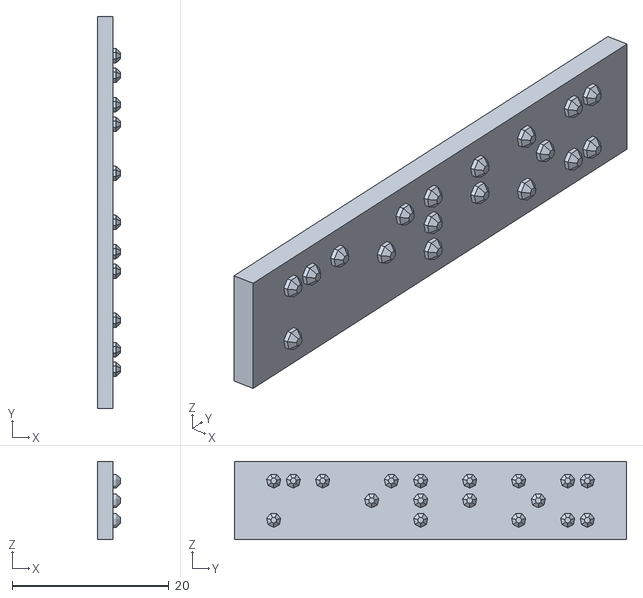
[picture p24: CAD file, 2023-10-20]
Build_Files/3D_Printing_Files/mailBoxLabel.stl
2.92 x 50.0 x 10.0

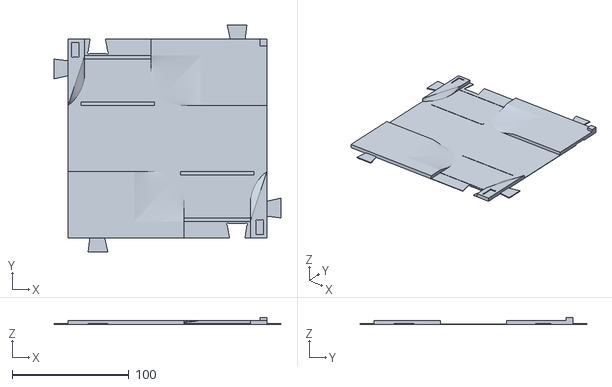
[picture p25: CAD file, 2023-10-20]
Build_Files/3D_Printing_Files/offsetIntersection.stl
194.3 x 194.3 x 6.00

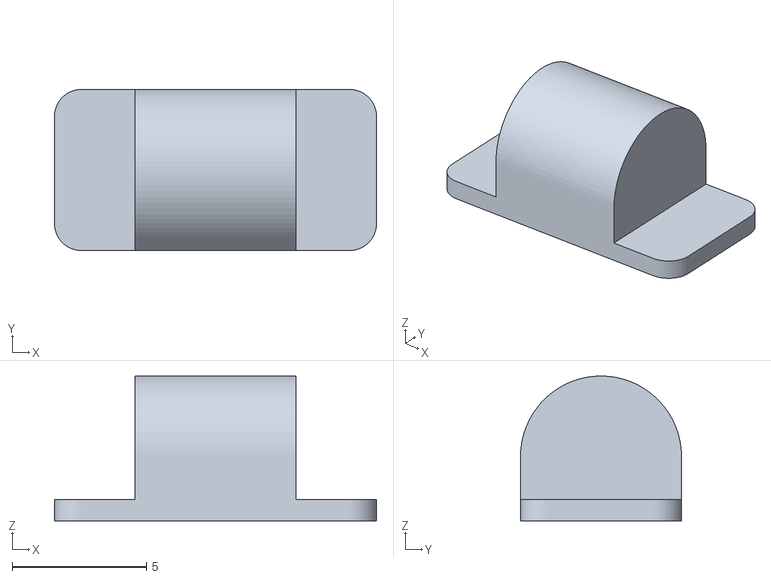
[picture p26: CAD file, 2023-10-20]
Build_Files/3D_Printing_Files/busStopPiece.stl
12.0 x 6.00 x 5.40

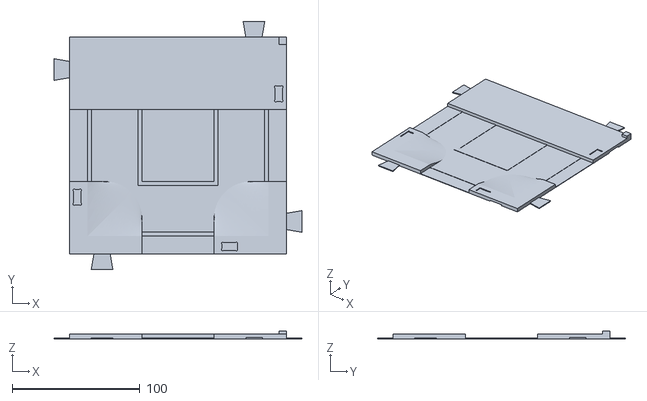
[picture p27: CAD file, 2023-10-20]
Build_Files/3D_Printing_Files/TIntersectionMap.stl
194.3 x 194.3 x 6.00

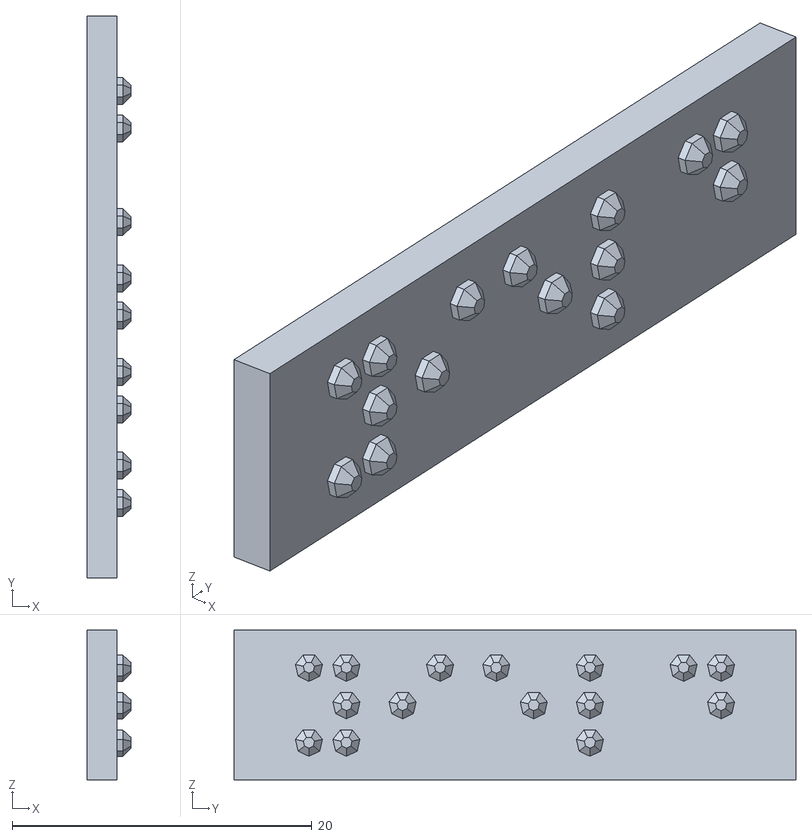
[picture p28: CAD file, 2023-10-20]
Build_Files/3D_Printing_Files/yieldSignLabel.stl
2.92 x 37.5 x 10.0

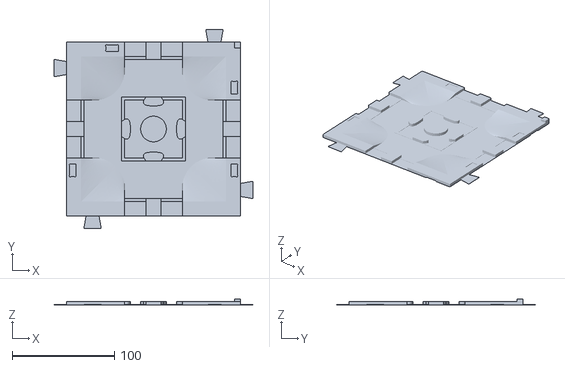
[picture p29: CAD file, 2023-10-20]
Build_Files/3D_Printing_Files/roundaboutMap.stl
194.3 x 194.3 x 6.00

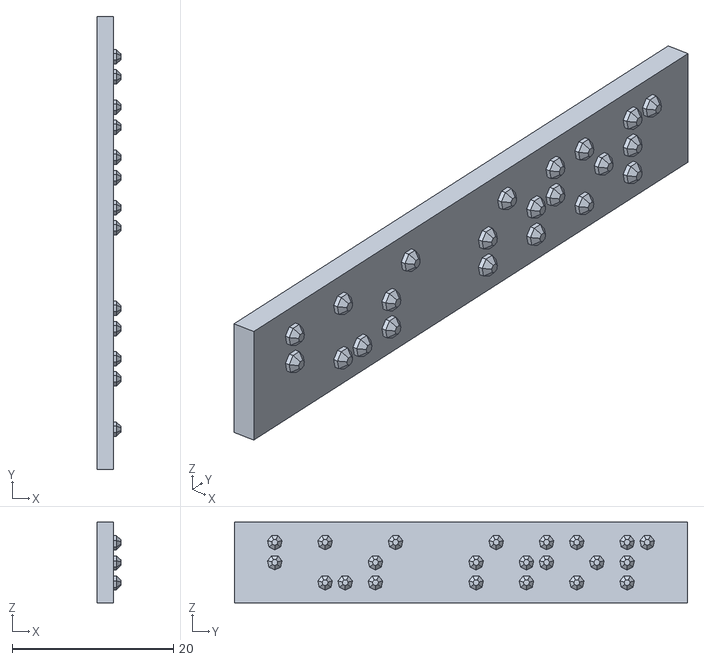
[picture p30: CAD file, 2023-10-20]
Build_Files/3D_Printing_Files/busStopLabel.stl
2.92 x 56.2 x 10.0

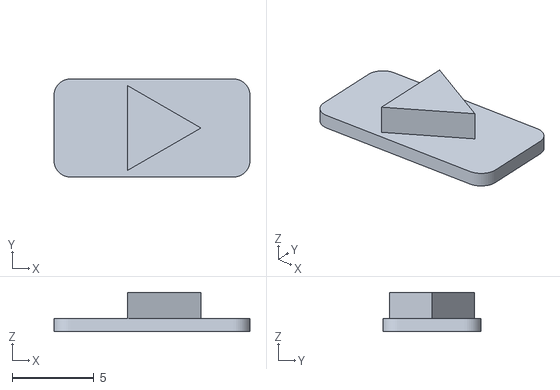
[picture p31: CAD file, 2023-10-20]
Build_Files/3D_Printing_Files/yieldSignPiece.stl
12.0 x 6.00 x 2.40

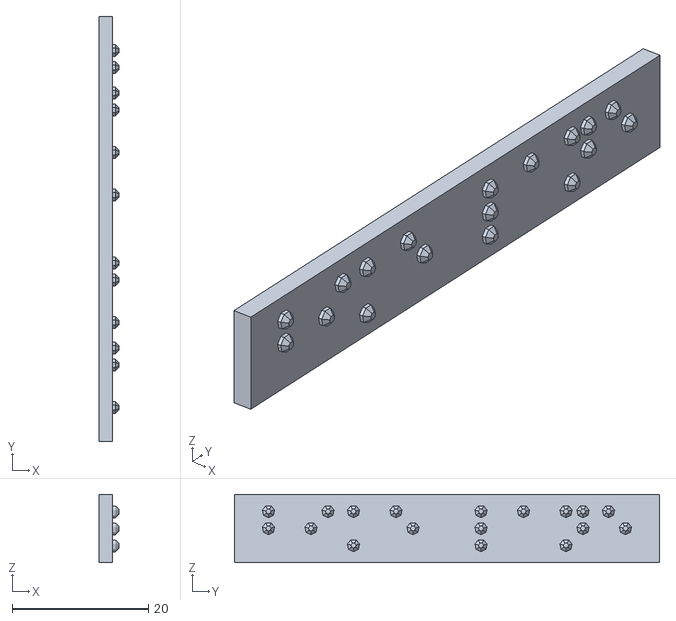
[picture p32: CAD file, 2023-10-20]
Build_Files/3D_Printing_Files/BikeLaneLabel.stl
2.92 x 62.5 x 10.0

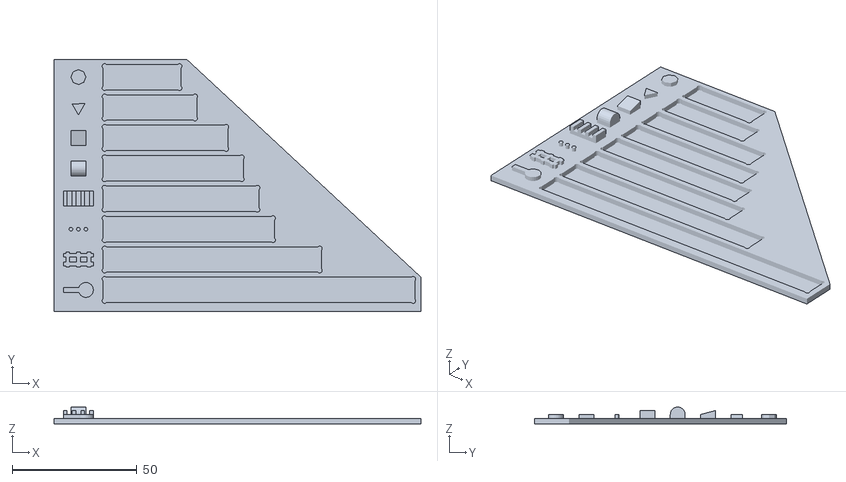
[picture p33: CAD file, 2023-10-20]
Build_Files/3D_Printing_Files/tactileMapsLegend.stl
147.2 x 101.2 x 6.80

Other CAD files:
Build_Files/3D_Printing_Files/railCrossingPiece.stl
Build_Files/3D_Printing_Files/stopLightPiece.stl
Build_Files/3D_Printing_Files/railCrossingLabel.stl
Build_Files/3D_Printing_Files/fourWayStop.stl
Build_Files/3D_Printing_Files/PedestrianCrossingLabel.stl
Build_Files/3D_Printing_Files/bikeLanePiece.stl
Build_Files/3D_Printing_Files/largeIntersection.stl
Build_Files/3D_Printing_Files/pedestrianCrossingPiece.stl
Build_Files/3D_Printing_Files/stopLightLabel.stl
Design_Files/CAD_Design_Files/TIntersectionMap.f3z
Design_Files/CAD_Design_Files/TactileMapsParameters.f3d
Design_Files/CAD_Design_Files/bikeLanePiece.f3z
Design_Files/CAD_Design_Files/busStopPiece.f3z
Design_Files/CAD_Design_Files/fourWayStopMap.f3z
Design_Files/CAD_Design_Files/largeIntersectionMap.f3z
Design_Files/CAD_Design_Files/mailBoxPiece.f3z
Design_Files/CAD_Design_Files/offsetIntersectionMap.f3z
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

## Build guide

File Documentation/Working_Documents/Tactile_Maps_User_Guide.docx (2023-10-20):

## Introduction

These are 3D printed Tactile Maps for people with visual impairments. The general maps represent different intersections and common road signs and landmarks. The maps can be used to learn how to navigate different intersections and plan routes between places.

It is important to note these maps are not designed to be an independent navigational tool. They are intended to help teach common features of different types of road intersections to help users with visual impairment learn to recognize different intersections. Relying on the maps for navigation could cause potential harm to users, such as getting lost or misidentifying an intersection.

## Features

All the tactile maps have the road surface as the lowest surface, with any features raised above that. Painted pedestrian crossing lines are the second lowest feature and are raised to be felt by the user. Sidewalks and curbs are the third lowest feature, with curb cuts represented as gradual height increases and curbs as sudden changes in height (as they are in the real world). The features that can be slotted into the cut-outs on the sidewalks are the second highest level, allowing users to feel where and what a traffic sign may be. The highest feature on the map is a square in the top-right corner. This is used to orient the map and can represent North-East if planning a route. There are also tabs and cut-outs on the maps to connect and align them if they are being used together for route planning. All features are shown in the figures below.

A tactile map of a large intersection. Different features are highlighted with different shaped boxes. A tab on the side used to connect maps together is circled in red, a stop sign piece is surrounded by a red rectangle, and the orientation indicator is surrounded by a red triangle.

The tabs on the sides of the maps are used to connect maps together. One of the tabs (top left) is circled in red. There are red pieces representing a stop sign, stop light, yield sign, and mailbox added to the map. The stop sign piece is surrounded by a red square. These pieces can be interchanged among maps and positions on the maps. The orientation square in the top right is surrounded by a red triangle.

Hook side of hook and loop tape attached to the back of a tactile map. The cut-outs where tabs connect adjacent maps are circled in red.

The bottom of the map shows the corresponding cut-outs for the tabs on the sides. The tabs fit into the cut-outs to prevent the maps from shifting while users run their fingers over them. The cut-out on the top left has been circled in red.

There is also a legend with Braille labels to help users identify different features such as traffic signs/signals.

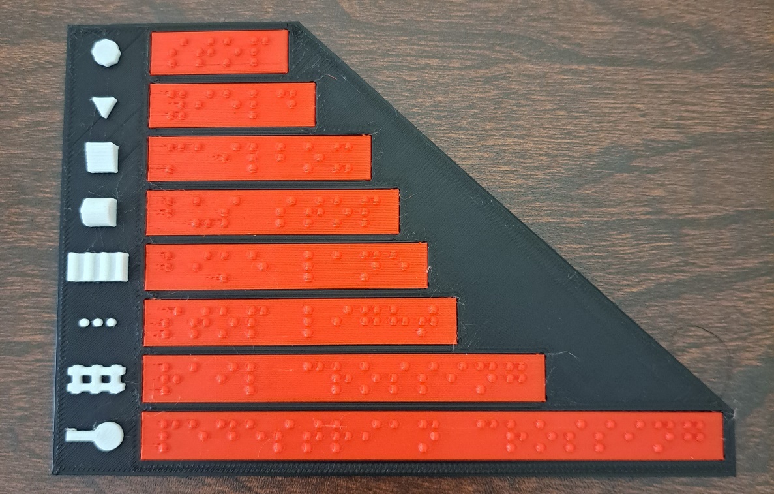
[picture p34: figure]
The legend and labels for the tactile maps. The Braille labels have been printed in red, the background in black, and the features in white.

From top to bottom the symbols represent a stop sign, a yield sign, a mailbox, a bus stop, a bike lane, a stop light, rail tracks, and a pedestrian crossing. The labels read: “stop”, “yield”, “mailbox”, “bus stop”, “bike lane”, “stop light”, “rail crossing”, and “pedestrian crossing”.

## Usage

Use the map on a surface where it will not slide around as the user runs their hands over the map. If the map has hook and loop tape, the maps can be attached to any surface the hook side will attach to, including carpet or tactile map diagramming kit backboards. Insert the desired traffic sign/signal pieces into the spaces on the tactile maps being used. The pieces should fit snuggly into the cut-outs on the tops of the maps and not get knocked out when running your hand over the features. They should still be easy to remove and change different pieces.

There is a raised square in the top-right corner of the map to help users orient to the direction of the maps. For example, this corner could represent North-East.

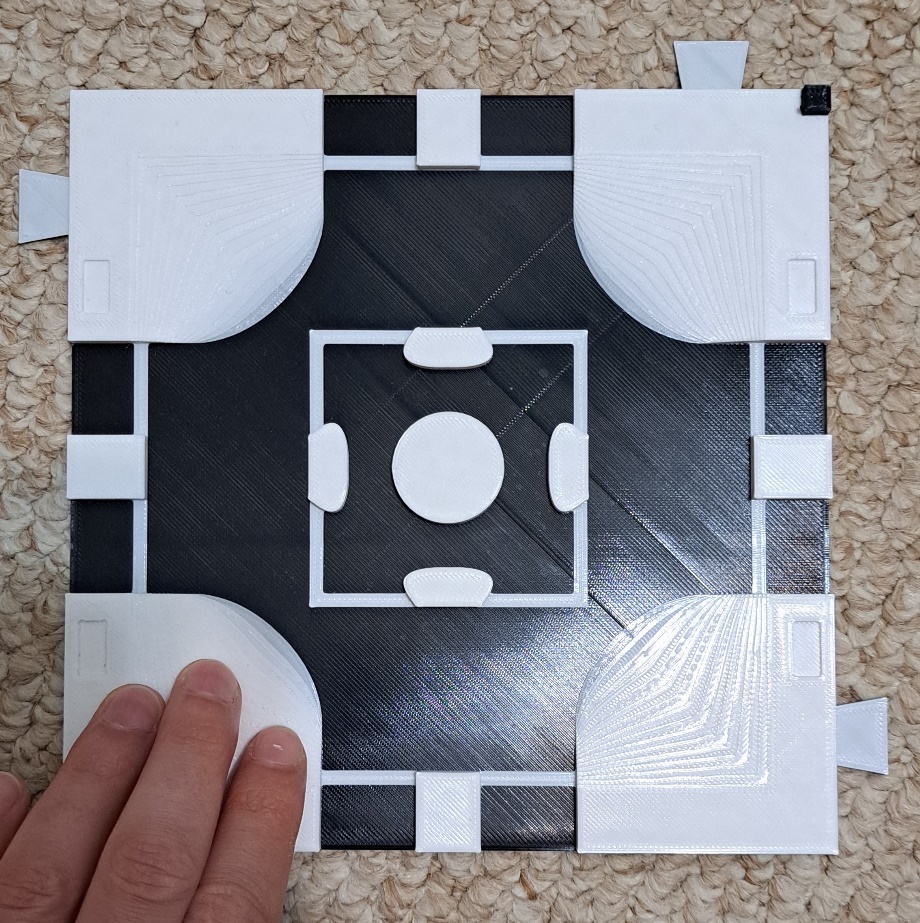
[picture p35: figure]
A user running their hand across the bottom of a tactile map representing a roundabout. The map has been attached to a carpet using hook and loop tape.

A user will run their hands over the maps to feel the different road features, including crosswalk lines, sidewalks/pavement, and traffic signs/signals. If they are unsure what a feature represents, they can consult the legend if they read Braille. If they do not read Braille, the different signs and signals are shown below.

3D printed features that represent from left to right: Stop signs, yield signs, mailboxes, bus stops, bike lanes, stop signs, railroad crossings, and pedestrian crossings.

3D printed features that represent from left to right: Stop signs, yield signs, mailboxes, bus stops, bike lanes, stop signs, railroad tracks, and pedestrian crossings.

Maps can also be connected to represent a route between places in a city. For example, if someone had to walk through an offset intersection then to a pedestrian crossing, the two maps could be connected as shown below.

Two tactile maps connected together by the tabs on the edges of the maps. The two maps represent an offset intersection and pedestrian crossing.

## Compatibility

If the tactile maps have hook and loop tape attached to them, they can be affixed to backings such as carpet or tactile map diagramming kits to keep them from sliding while in use.

## Specifications

The default map size is 17x17x0.6 cm. Each map weighs between 38 and 53 g. The pieces that can be placed on the maps are 1.2x0.6x0.24 cm and weigh 0.125 g each. The legend is 14.7x10x0.7 cm and weighs 28 g, including all the labels.

## Cleaning

All maps and pieces can be cleaned with any cleaning solution that will not degrade plastic.

© 2023 by Neil Squire. This work is licensed under the CC BY SA 4.0 License: http://creativecommons.org/licenses/by-sa/4.0 Files available at https://makersmakingchange.com/project/tactile-maps/ Page 2 of 3

V1.0 | May 2023 Tactile Maps user Quick Guide

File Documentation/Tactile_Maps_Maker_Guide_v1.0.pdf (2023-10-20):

V1.0 | May 2023

## Tactile Maps

## MAKER GUIDE

© 2023 by Neil Squire. (https://neilsquire.ca/)
This work is licensed under the CC BY SA 4.0 License: http://creativecommons.org/licenses/by-sa/4.0 Files available at https://makersmakingchange.com/project/tactile-maps/

### Overview

This document contains the necessary information to build Tactile Maps.

### Contents

## MAKER GUIDE

© 2023 by Neil Squire. (https://neilsquire.ca/)

### Maker Checklist

This list provides an overview of the steps required to build and deliver Tactile Maps.

### Maker To Do List

Read through the Assembly Guide to become familiar with required components, tools, supplies, safety gear, and overall assembly steps.
Talk to User about customization options (e.g., color, any special requests, etc.)
Order hardware components
Gather tools, supplies, and safety equipment.
Assemble the device
Test device
Print “User Guide”

### Items to Give to User

Assembled, tested device
“User Guide”

### Tool List

- Scissors (optional)
- Hobby knife (optional)

## MAKER GUIDE

© 2023 by Neil Squire. (https://neilsquire.ca/)

### Customization Guide

The user may only want specific maps and/or features for the maps. Ask the user which maps and features they want, and how many of each they would like.

Ask the user if they want the map printed in a specific colour, and/or in two-tones. Users with partial sight may be able to see high contrast features on the map. If printing in two-tones, we recommend the following colour combinations:

- Black and white
- Black and bright yellow
- Dark blue and white
- Dark blue and bright yellow

You may also ask the user if they prefer a brighter colour on a darker background, or a darker colour on a lighter background.

The user may also want to be able to attach the maps to a surface using hook and loop tape. Ask the user if they would like hook and loop tape attached to the back of the maps and/or legend. If they do, place the hook side (scratchy side) of the hook and loop tape to the map and/or legend.

## MAKER GUIDE

© 2023 by Neil Squire. (https://neilsquire.ca/)

### 3D Printing Guide

### 3D Printing Summary

Metrics | Single Unit
Total Print Time (min) | 2,122
Total Number of Components | 23
Typical Total Mass (g) | 289
Typical Number of Print Setups | 16

### 3D Printing Settings

Print File Name | Qty | Total Print Time (hr:min) | Mass (g) | Infill (%) | Support(Y/N) | Layer Height/ Nozzle Diameter(mm) | Notes
tactile Maps Legend.stl | 1 | 1:56 | 14 | 20 | N | 0.2/0.4 | - Print in orientation given in STL - If printing in two-tones, add filament switch at layer 12 (2.4 mm)
fourWayStop.stl | 1 | 4:40 | 38 | 20 | N | 0.2/0.4 | - Print in orientation given in STL - If printing in two-tones, add filament switch at layers 3 (0.6 mm) and 19 (3.8 mm)
large Intersection.stl | 1 | 5:16 | 42 | 20 | N | 0.2/0.4 | - Print in orientation given in STL - If printing in two-tones, add filament switch at layers 3 (0.6 mm) and 19 (3.8 mm)

## MAKER GUIDE

© 2023 by Neil Squire. (https://neilsquire.ca/)

offset Intersection.stl | 1 | 4:39 | 39 | 20 | N | 0.2/0.4 | - Print in orientation given in STL - If printing in two-tones, add filament switch at layers 3 (0.6 mm) and 19 (3.8 mm)
pedestrian Crossing Map.stl | 1 | 6:02 | 53 | 20 | N | 0.2/0.4 | - Print in orientation given in STL - If printing in two-tones, add filament switch at layers 3 (0.6 mm) and 19 (3.8 mm)
roundabout Map.stl | 1 | 5:17 | 43 | 20 | N | 0.2/0.4 | - Print in orientation given in STL - If printing in two-tones, add filament switch at layers 3 (0.6 mm) and 19 (3.8 mm)
TIntersection.stl | 1 | 5:24 | 47 | 20 | N | 0.2/0.4 | - Print in orientation given in STL - If printing in two-tones, add filament switch at layers 3 (0.6 mm) and 19 (3.8 mm)
bike LanePiece.stl | 1 | 0:03 | 0.125 | 20 | N | 0.2/0.4 | - Print in orientation given in STL

## MAKER GUIDE

© 2023 by Neil Squire. (https://neilsquire.ca/)

bike LaneLabel.stl | 1 | 0:13 | 1 | 20 | N | 0.2/0.4 | - Print in orientation given in STL
bus StopPiece.stl | 1 | 0:02 | 0.125 | 20 | N | 0.2/0.4 | - Print in orientation given in STL
bus StopLabel.stl | 1 | 0:12 | 1 | 20 | N | 0.2/0.4 | - Print in orientation given in STL
mail BoxPiece.stl | 1 | 0:02 | 0.125 | 20 | N | 0.2/0.4 | - Print in orientation given in STL
mail BoxLabel.stl | 1 | 0:11 | 1 | 20 | N | 0.2/0.4 | - Print in orientation given in STL
pedestrian CrossingPiece.stl | 1 | 0:02 | 0.125 | 20 | N | 0.2/0.4 | - Print in orientation given in STL
pedestrian CrossingLabel.stl | 1 | 0:26 | 3 | 20 | N | 0.2/0.4 | - Print in orientation given in STL
rail CrossingPiece.stl | 1 | 0:02 | 0.125 | 20 | N | 0.2/0.4 | - Print in orientation given in STL
rail CrossingLabel.stl | 1 | 0:18 | 2 | 20 | N | 0.2/0.4 | - Print in orientation given in STL
stop LightPiece.stl | 1 | 0:01 | 0.125 | 20 | N | 0.2/0.4 | - Print in orientation given in STL
stop LightLabel.stl | 1 | 0:14 | 2 | 20 | N | 0.2/0.4 | - Print in orientation given in STL
stop SignPiece.stl | 1 | 0:01 | 0.125 | 20 | N | 0.2/0.4 | - Print in orientation given in STL
stop SignLabel.stl | 1 | 0:10 | 1 | 20 | N | 0.2/0.4 | - Print in orientation given in STL
yield SignPiece.stl | 1 | 0:01 | 0.125 | 20 | N | 0.2/0.4 | - Print in orientation given in STL

## MAKER GUIDE

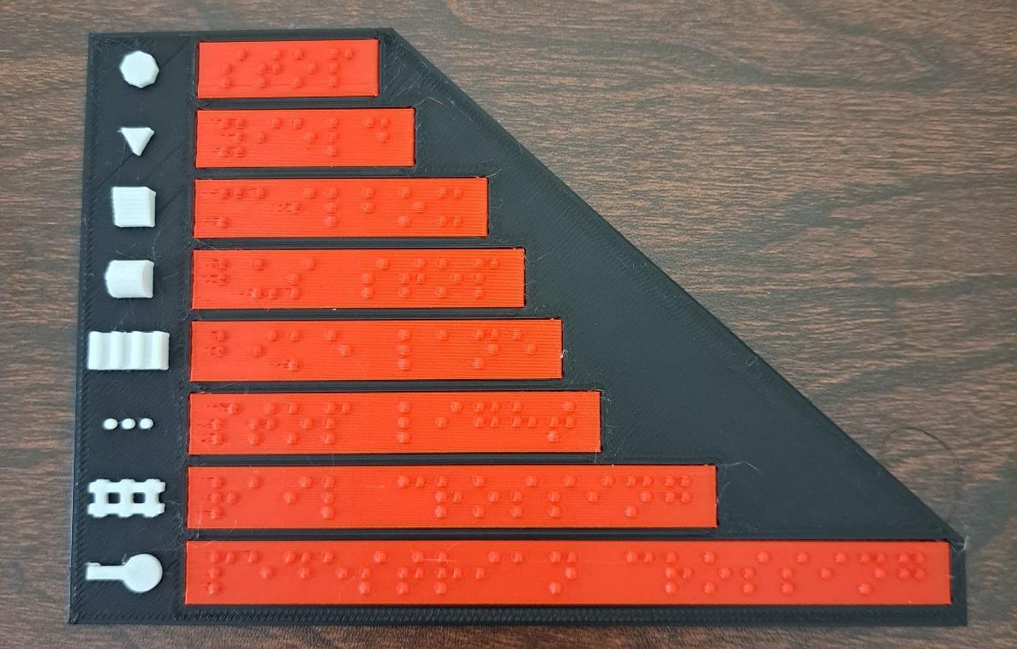
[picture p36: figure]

© 2023 by Neil Squire. (https://neilsquire.ca/)

yield
SignLabel.stl
1 | 0:10 | 1 | 20 | N | 0.2/0.4 | - Print in orientation given in STL

### Post-Processing

Clean up any stringing or rough edges that may have occurred.

### Examples of Quality Prints

Photo of Legend and Labels

Figure 1: Legend and Braille labels. The labels have been printed separately in red to give contrast with the background. The legend was printed in one piece with a filament change to contrast the features and the background.

From top to bottom the symbols represent a stop sign, a yield sign, a mailbox, a bus stop, a bike lane, a stop light, rail tracks, and a pedestrian crossing. The labels read: “stop”, “yield”, “mailbox”, “bus stop”, “bike lane”, “stop light”, “rail crossing”, and “pedestrian crossing”.

## MAKER GUIDE

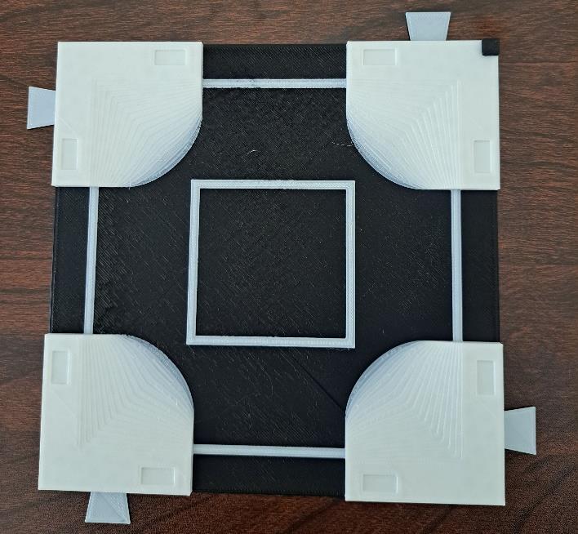
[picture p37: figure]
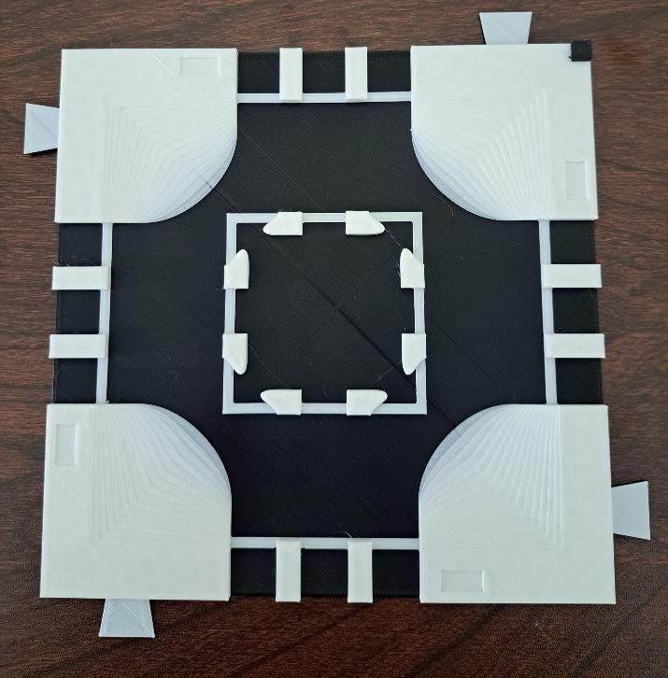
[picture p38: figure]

© 2023 by Neil Squire. (https://neilsquire.ca/)

Photo of Four Way Stop Map

Photo of Large Intersection Map

## MAKER GUIDE

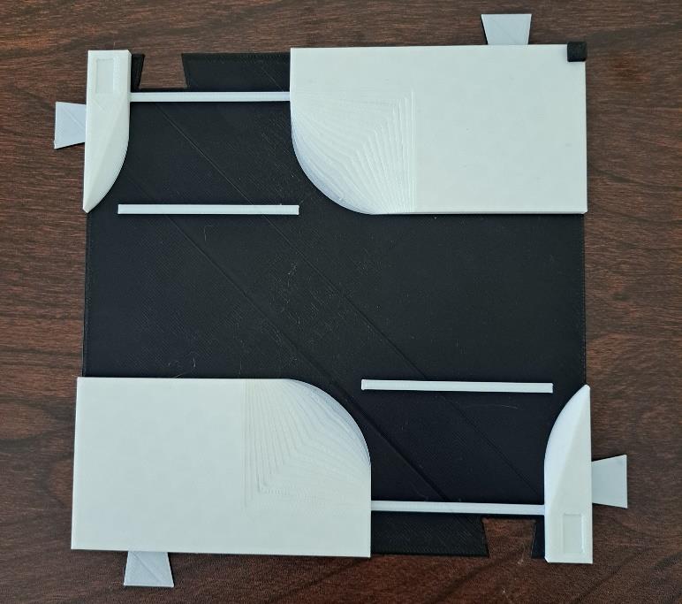
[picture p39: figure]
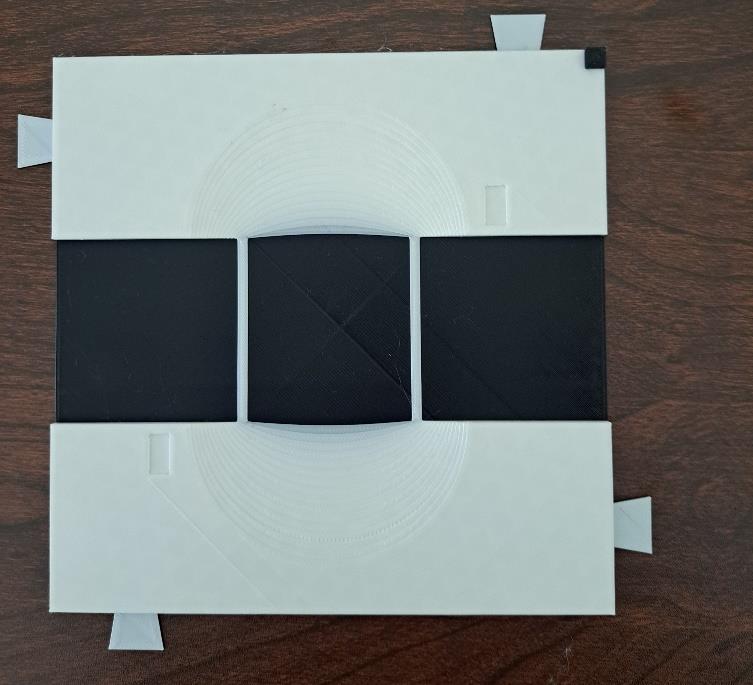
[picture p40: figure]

© 2023 by Neil Squire. (https://neilsquire.ca/)

Photo of Offset Intersection Map

Photo of Pedestrian Crossing Map

## MAKER GUIDE

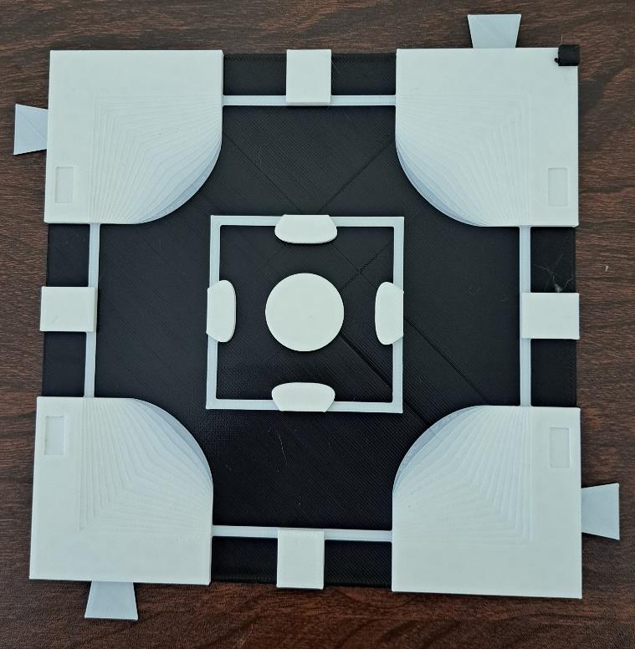
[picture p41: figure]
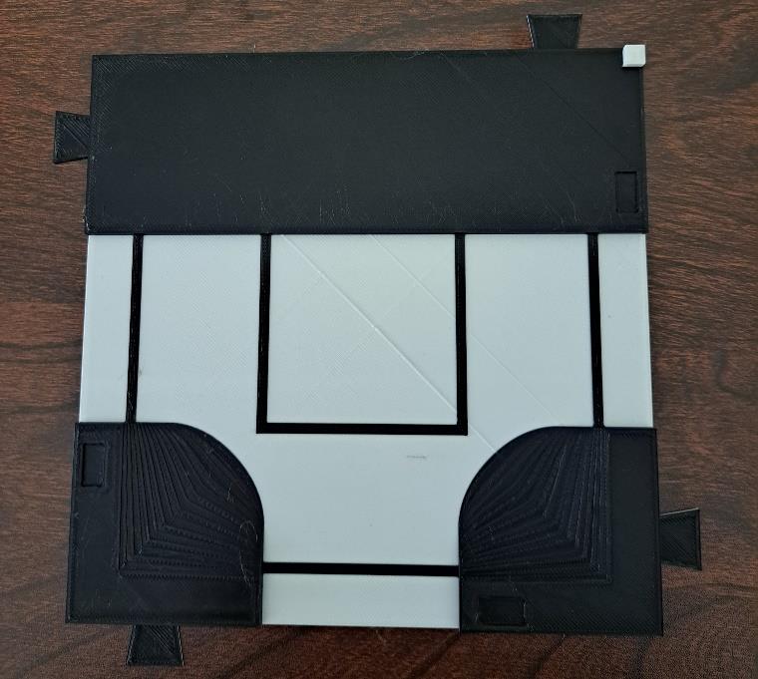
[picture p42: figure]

© 2023 by Neil Squire. (https://neilsquire.ca/)

Photo of Roundabout Map

Photo of T Intersection Map

## MAKER GUIDE

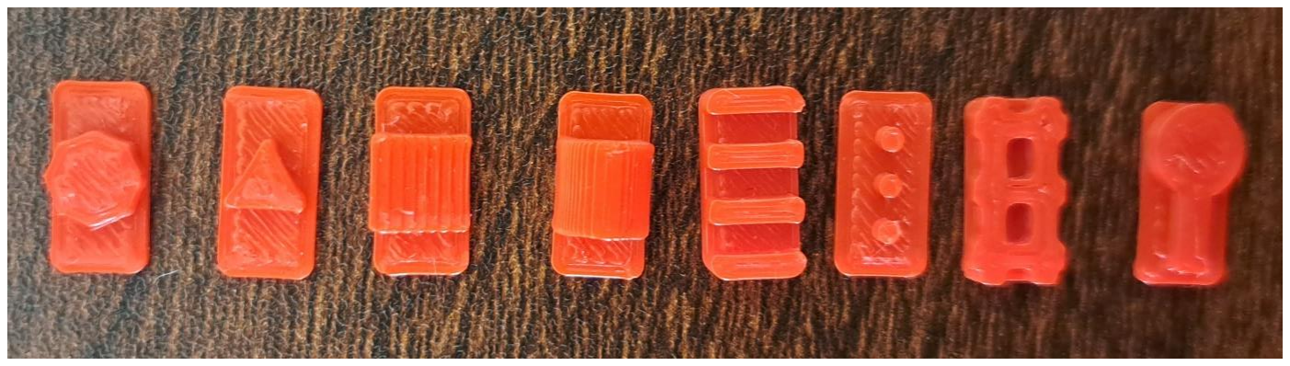
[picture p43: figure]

© 2023 by Neil Squire. (https://neilsquire.ca/)

Photo of Features

3D printed features that represent from left to right: Stop signs, yield signs, mailboxes, bus stops, bike lanes, stop lights, railroad tracks, and pedestrian crossings.

## MAKER GUIDE

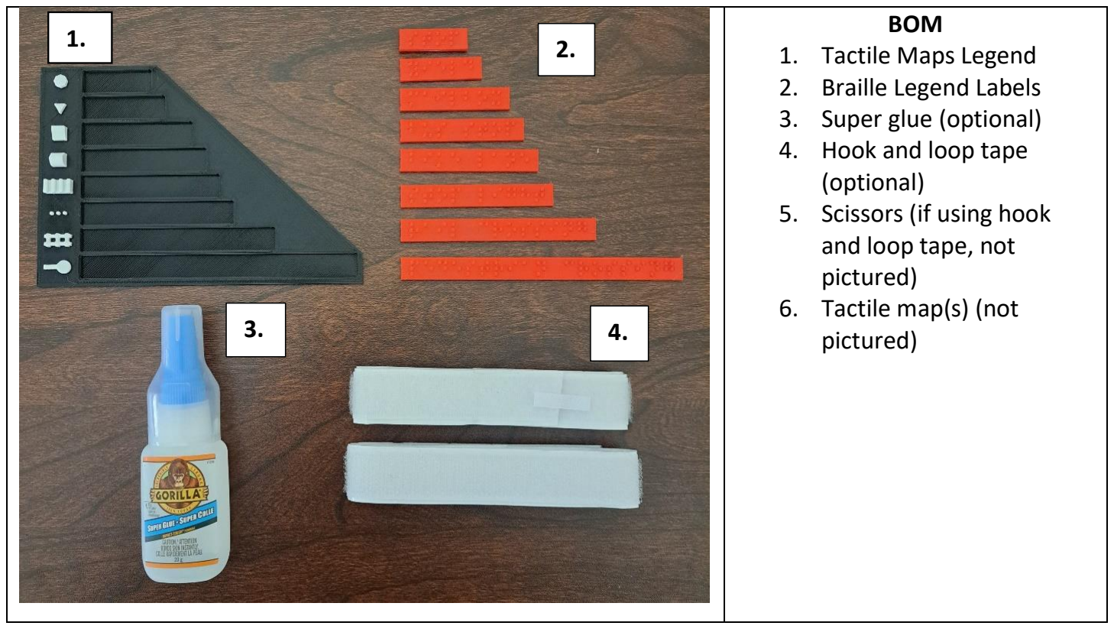
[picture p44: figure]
BOM 1. Tactile Maps Legend 2. Braille Legend Labels 3. Super glue (optional) 4. Hook and loop tape (optional) 5. Scissors (if using hook and loop tape, not pictured) 6. Tactile map(s) (not pictured)

© 2023 by Neil Squire. (https://neilsquire.ca/)

### Assembly Guide

### Required Components

### Required Tools

- Super glue (optional)
- Scissors (if using hook and loop tape)

### Required Personal Protective Equipment (PPE)

- Safety glasses
Step 1: Gather materials and tools
Gather all materials and tools listed in the Required Components. Ensure you also have any tactile maps the user requested. They are not pictured in the Required Components as there are six general maps a user may request.
Step 2: Insert Braille labels into Tactile Maps Legend.
Insert the Braille labels into the corresponding spaces on the legend. The labels will fit into their corresponding space snuggly. Ensure the labels are the correct orientation, and that the raised Braille characters are exposed. If you cannot read Braille, refer to the Photo of Legend and

## MAKER GUIDE

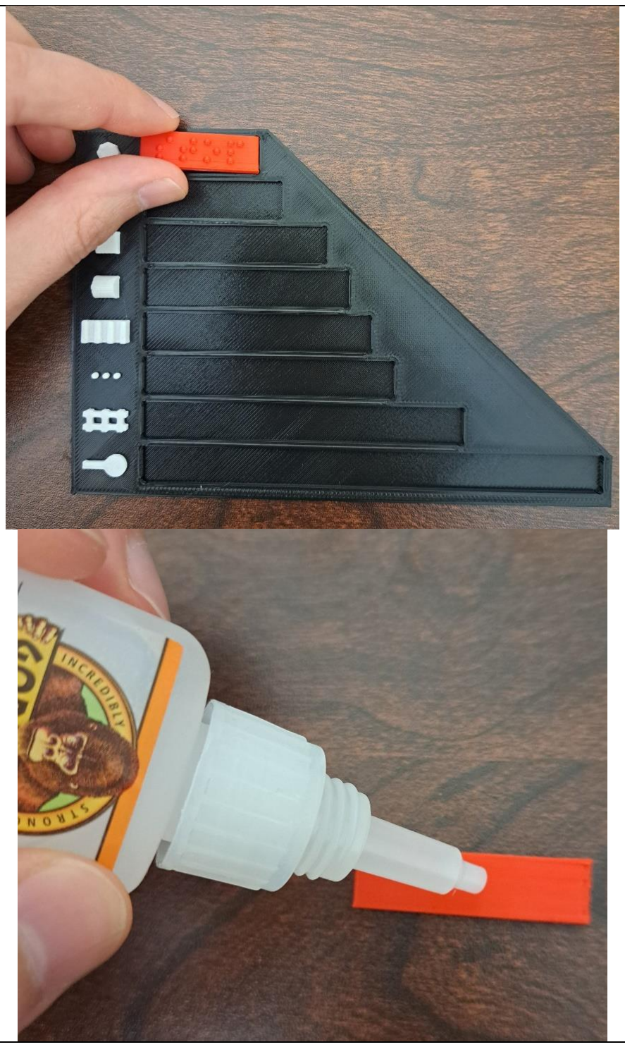
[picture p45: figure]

© 2023 by Neil Squire. (https://neilsquire.ca/)

Labels under Examples of Quality Prints, or the labels in the Required Components as they are in the correct orientation.

If a label is loose in its space, you may apply some super glue to secure the label in the legend.

Place all labels into the legend. If the user did not request hook and loop tape, assembly is now complete. If they did request hook and loop tape, repeat the following steps for all maps the user requested.

## MAKER GUIDE

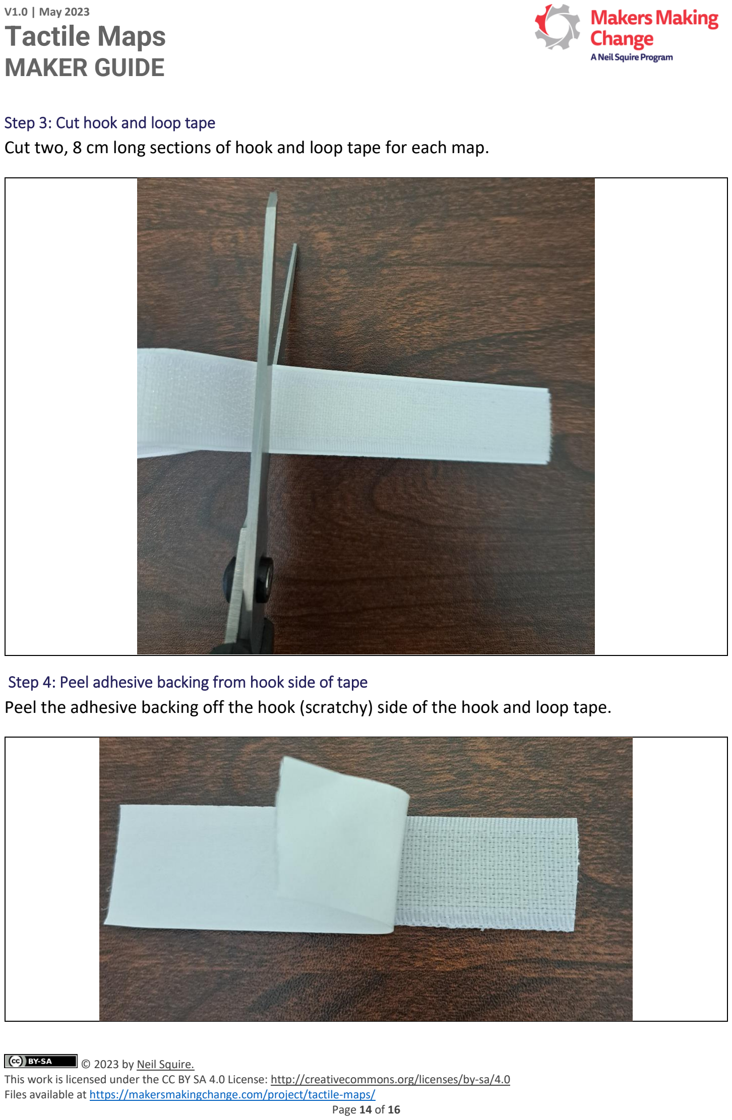
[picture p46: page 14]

© 2023 by Neil Squire. (https://neilsquire.ca/)

Step 3: Cut hook and loop tape
Cut two, 8 cm long sections of hook and loop tape for each map.
Step 4: Peel adhesive backing from hook side of tape
Peel the adhesive backing off the hook (scratchy) side of the hook and loop tape.

## MAKER GUIDE

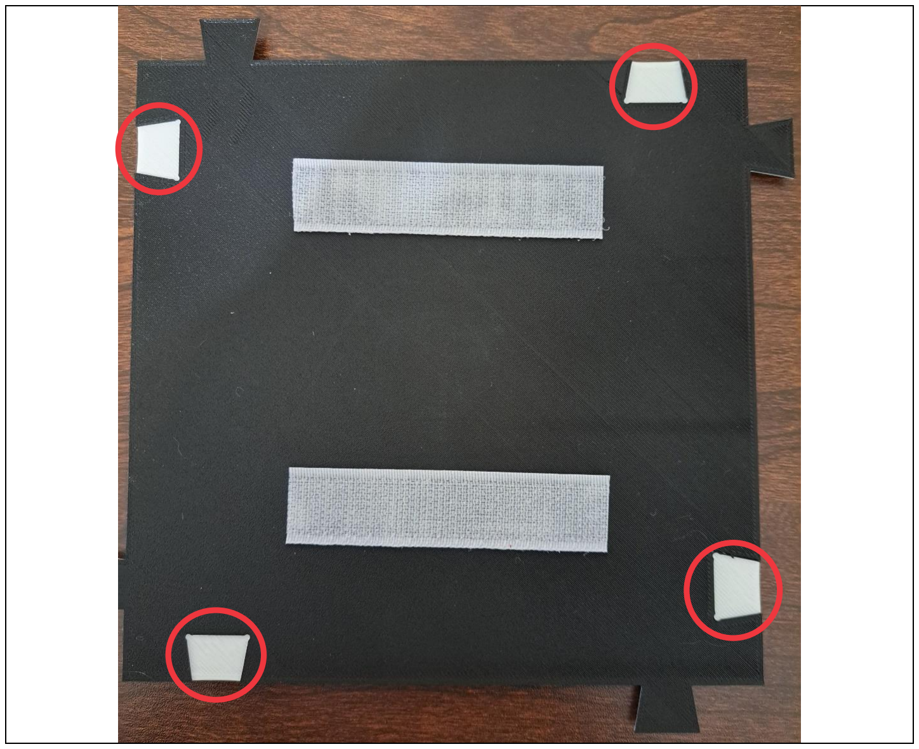
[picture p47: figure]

© 2023 by Neil Squire. (https://neilsquire.ca/)

Step 5: Attach hook side of tape to map
Attach the hook side of the hook and loop tape to the back of the tactile map. Attach two pieces per map. Ensure you do not cover the cut-outs where the tabs secure multiple maps together (circled in red in the picture).

Repeat Steps 4 and 5 for all maps the user requested, and the legend if they requested hook and loop tape on it as well.

### Testing

Place the traffic sign/signal pieces into the cut-outs on the tops of the maps. They should fit snuggly and not fall out when you run your hand over them, but still be easy to pop out of the cut-outs.

## MAKER GUIDE

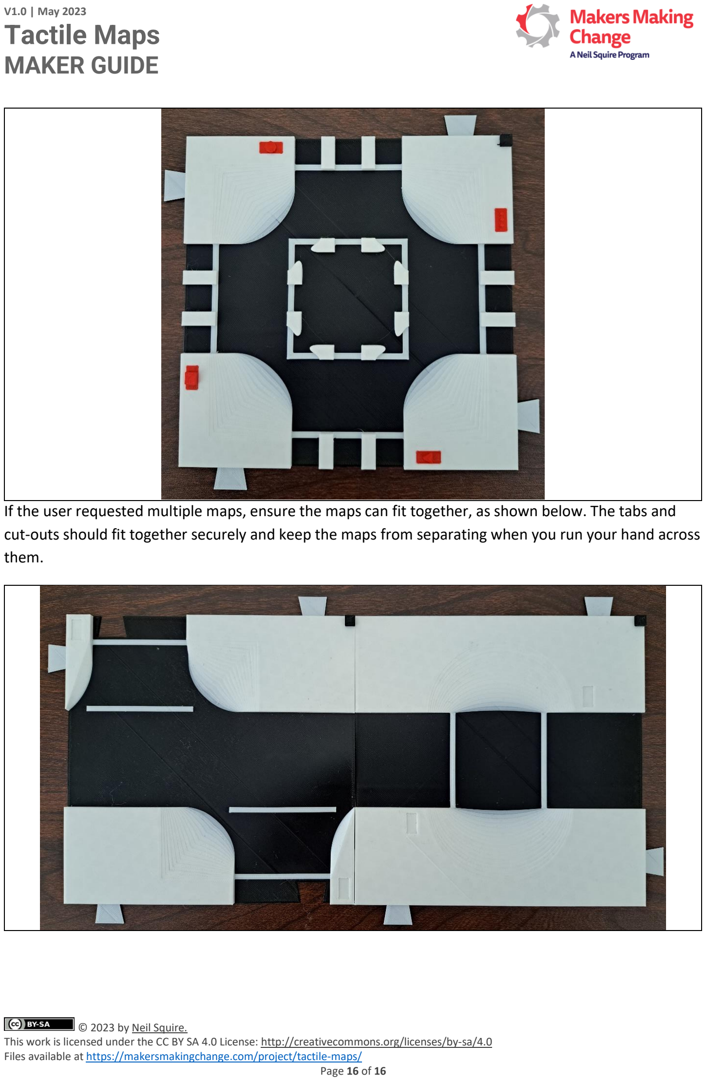
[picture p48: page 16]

© 2023 by Neil Squire. (https://neilsquire.ca/)

If the user requested multiple maps, ensure the maps can fit together, as shown below. The tabs and cut-outs should fit together securely and keep the maps from separating when you run your hand across them.

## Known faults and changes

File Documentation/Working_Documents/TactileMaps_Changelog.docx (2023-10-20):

# Version 1.0 | Date 05/18/2023

- Initial designs by Stephan Dobri – Makers Making Change
- Documentation by Neil Squire Society/Makers Making Change

© 2023 by Neil Squire. This work is licensed under the CC BY SA 4.0 License: http://creativecommons.org/licenses/by-sa/4.0 Files available at https://makersmakingchange.com/project/tactile-maps/ Page 1 of 1

V1.0 | May 2023 Tactile Maps changelog
